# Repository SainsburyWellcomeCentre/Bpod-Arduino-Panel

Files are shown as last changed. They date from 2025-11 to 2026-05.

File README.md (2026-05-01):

# Bpod Arduino Panel



A 58 I/O ports Bpod Module for neuroscience experiments.

> **Note:** To use this module with timing synchronisation, a Bpod state machine is required. Please refer to the [Bpod documentation](https://sanworks.github.io/Bpod_Wiki/) for more information.

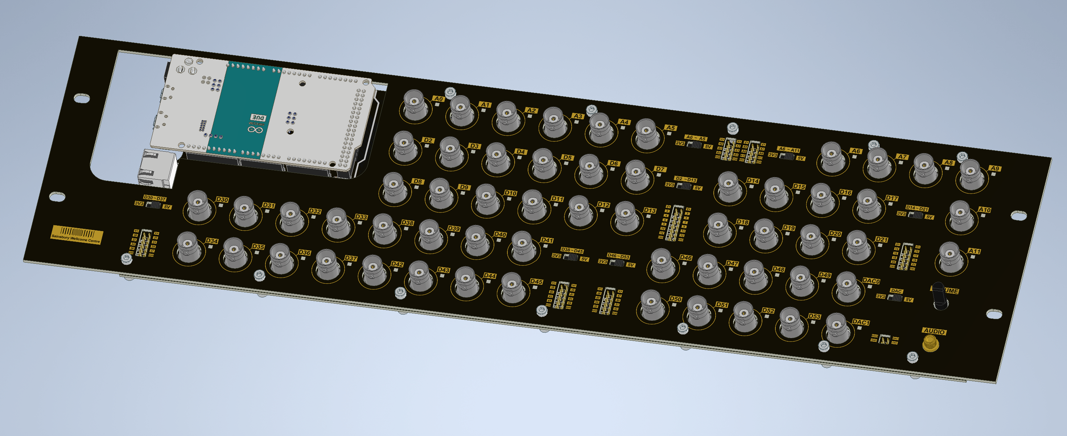
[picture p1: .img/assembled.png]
Assembled


The Bpod Arduino Panel is a Bpod expansion module powered by an Arduino Due. Equipped with 44 digital input/output ports, 12 analogue input ports, and 2 analogue output ports, it can drive various behavioural devices such as lights, speakers, valve drivers, and sensors. Each group of ports can be configured between 5V and 3.3V logic levels. This module is specifically designed for compatibility with the Bpod ecosystem, enabling users to synchronise timing when controlling large numbers of devices.

## 🔧 Features

- 44 digital input/output ports + 14 analogue ports (12 in, 2 out)
- Configurable logic levels (5V/3.3V)
- One 3.5mm audio output drives up to consumer line level (-10 dBV / 0.316 Vrms).
- 3U rack mountable panel

## 🌐 View Online (eCAD)

View the complete electronic design project online via [Altium 365 Viewer](https://sainsburywellcomecentre.github.io/fablabs-documentation/#Bpod-Arduino-Panel)

## 🚀 Getting Started

1. Connect the Bpod Arduino Panel to your computer via USB.
2. Open the Arduino IDE and select the appropriate board and port.
3. Upload the firmware to the Bpod Arduino Panel.
4. Connect the Bpod Arduino Panel to the Bpod state machine using an RJ45 cable.

## 🚀 I/O Port Layout

The following image provides an overview of the port layout and their respective functions.

1. Arduino Due Board
2. RJ45 Connector for Bpod communication
3. Digital I/O Ports (5 groups of 8/12, 44 total)
4. Analogue Input Ports (2 groups of 6, 12 total)
5. Analogue Output Ports (2 total) and Audio Output (3.5mm jack)

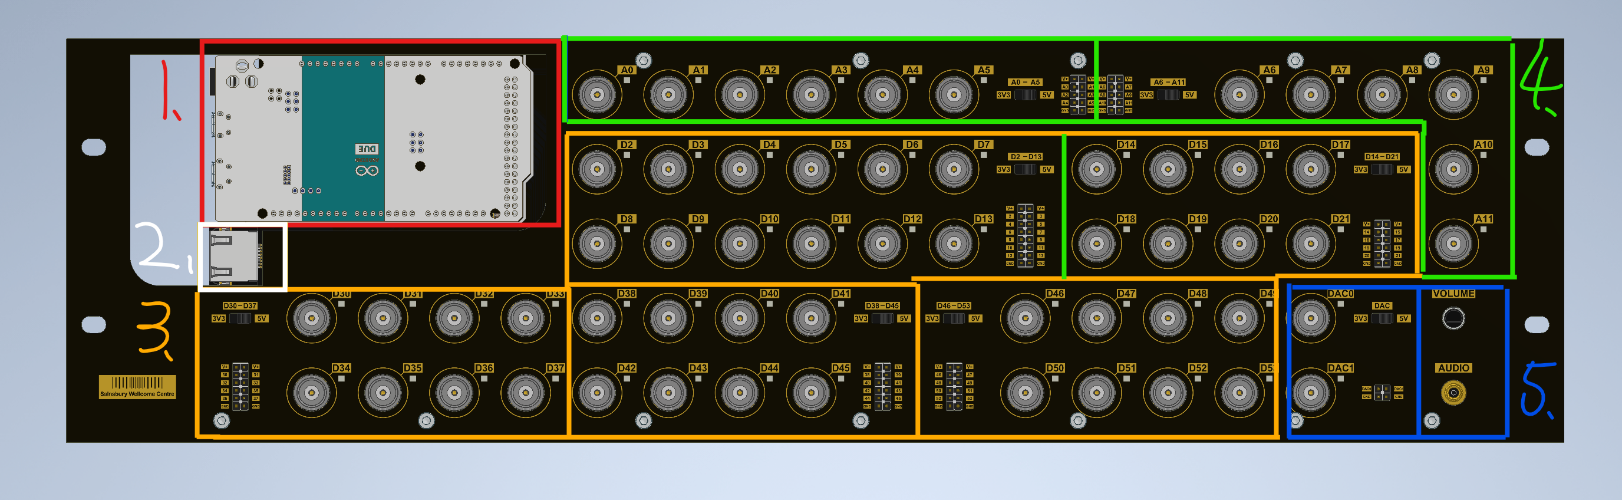
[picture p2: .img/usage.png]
port description


## ⚙️ Voltage Configuration

The max voltage levels for all the I/O are configured by the on-board switches. Each group can be configured between 3.3v and 5V. The ports on the module are grouped as follows:

- D2 to D13
- D14 to D21
- D30 to D37
- D38 to D45
- D46 to D53
- A0 to A5
- A6 to A11
- DAC0 and DAC1

## ⚙️ Firmware and Protocol

The firmware development is based on the Arduino platform, reference from the [Bpod shield](https://github.com/sanworks/Bpod_Gen2/tree/master/Examples/Firmware/Bpod%20Shield) firmware.

The operation code (opcode in Bpod Language) of the device is varied according to the firmware. The functionality of each port has to be pre-defined in the firmware. Please refer to the [opcode table](firmware/OPCODE_TABLE.md) for detailed information on available opcodes and their usage.

## 💻 Software Requirements

- **Altium Designer 24** or newer  
  Academic licenses available via [Altium Education](https://www.altium.com/education/)

- **Autodesk Inventor Pro 2025** or newer  
  Academic licenses via [Autodesk Education](https://www.autodesk.com/education/home)

- **Arduino IDE** (Download from [Arduino Software](https://www.arduino.cc/en/software))

## 📜 License

**Sainsbury Wellcome Centre hardware is released under** [Creative Commons Attribution-ShareAlike 4.0 International](http://creativecommons.org/licenses/by-sa/4.0/).

You are free to:

- **Share** — copy and redistribute the material in any medium or format
- **Adapt** — remix, transform, and build upon the material for any purpose

Under the following terms:

- **Attribution** — Give appropriate credit, link to the license, and indicate changes.
- **ShareAlike** — Distribute your contributions under the same license.
- **No additional restrictions** — Don’t apply legal or technological measures that prevent others from doing anything the license permits.

> For the full legal text, see [LICENSE](LICENSE).

## 💻 TODO

- [ ] Add Python program for standalone operation
- [ ] Add firmware upload instructions
- [ ] Add audio playback firmware example

## 📚 Credits

- **Bpod Shield**: [Sanworks LLC](https://sanworks.github.io/Bpod_Wiki/)
- **Protocol**: [ArCOM](https://github.com/sanworks/ArCOM)

## 🤝 Contributing

1. Fork the repository
2. Create a feature branch
3. Make your changes
4. Submit a pull request

## ❤ Contributors

 <a href = "https://github.com/sainsburywellcomecentre/Bpod-Arduino-Panel/graphs/contributors">
   Contributors
 </a>

## 📧 Contact

- **Author**: [@DCisHurt](https://github.com/DCisHurt)
- **Email**: [yuhsuan.chen@ucl.ac.uk](mailto:yuhsuan.chen@ucl.ac.uk)
- **Website**: [FabLabs](https://sainsburywellcomecentre.github.io/fablabs-documentation/#Bpod-Arduino-Panel)

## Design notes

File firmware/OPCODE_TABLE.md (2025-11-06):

# Opration Code Table

## ADIO.ino

The max voltage levels for all the I/O are configured by the on-board switches. Please refer to the hardware manual for more details.

## Digital Input Events

| Opcode     | Description                      |
| ---------- | -------------------------------- |
| 0x71, 0x72 | D2 Input Event High/Low          |
| 0x73, 0x74 | D3 Input Event High/Low          |
| 0x75, 0x76 | D4 Input Event High/Low          |
| ...        | (other opcodes remain unchanged) |
| 0x97, 0x98 | D21 Input Event High/Low         |

## Digital Input Enable/Disable

| Opcode | Description                      | Byte 1  | Byte 0   |
| ------ | -------------------------------- | ------- | -------- |
| 0x45   | Enable/Disable the digital input | channel | isEnable |

## Digital Output

| Opcode | Description                      | Byte 0 |
| ------ | -------------------------------- | ------ |
| 0x1E   | Set D30 Output High or Low       | logic  |
| 0x1F   | Set D31 Output High or Low       | logic  |
| 0x20   | Set D32 Output High or Low       | logic  |
| ...    | (other opcodes remain unchanged) | ...    |
| 0x35   | Set D53 Output High or Low       | logic  |

## Analog Input reading (16-bits resolution )

| Opcode | Description                      | Byte [1:0] |
| ------ | -------------------------------- | ---------- |
| 0x36   | read A0 voltage                  | ADC [1:0]  |
| 0x37   | read A1 voltage                  | ADC [1:0]  |
| ...    | (other opcodes remain unchanged) | ...        |
| 0x41   | read A11 voltage                 | ADC [1:0]  |

## Analog Output setting (16-bits resolution)

| Opcode | Description      | Byte [1:0] |
| ------ | ---------------- | ---------- |
| 0x42   | Set DAC0 voltage | DAC [1:0]  |
| 0x43   | Set DAC1 voltage | DAC [1:0]  |

## ModuleInfo

| Opcode | Description     |
| ------ | --------------- |
| 0xFF   | Get Module Info |

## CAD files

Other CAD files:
mCAD/HEX Spacer M3x7.ipt
mCAD/PCBA/ARDUINO DUE/ARDUINO DUE.iam
mCAD/PCBA/ARDUINO DUE/Berg Header - 1.27 x 10.ipt
mCAD/PCBA/ARDUINO DUE/Berg Header - 2.54 x 2.ipt
mCAD/PCBA/ARDUINO DUE/Berg Header Receptacle 2.54 x 10 - FCI - 66951-010LF.ipt
mCAD/PCBA/ARDUINO DUE/Berg Header Receptacle 2.54 x 36 - FCI - 66953-018LF.ipt
mCAD/PCBA/ARDUINO DUE/Berg Header Receptacle 2.54 x 8 - FCI - 66951-008LF.ipt
mCAD/PCBA/ARDUINO DUE/Capacitor - Nichicon - UUR1C101MCL1GS.ipt
mCAD/PCBA/ARDUINO DUE/Capacitor.ipt
mCAD/PCBA/ARDUINO DUE/LED - Kingbright - KPT-3216EC.ipt
mCAD/PCBA/ARDUINO DUE/MicroUSB AB - Hirose - ZX62D-AB-5P8.ipt
mCAD/PCBA/ARDUINO DUE/MicroUSB B - Hirose - ZX62D-B-5P8.ipt
mCAD/PCBA/ARDUINO DUE/Microchip - Atmel - SAM3X8EAU.ipt
mCAD/PCBA/ARDUINO DUE/Power Jack - Kycon - KLDHCX-0202-A.ipt
mCAD/PCBA/ARDUINO DUE/Switch - ESwitch - TLE3303.ipt
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

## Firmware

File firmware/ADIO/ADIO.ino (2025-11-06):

#include <Arduino.h>
#include <vector>


// Module setup

char moduleName[] = "BPod Panel"; // Name of module for manual override UI and state machine assembler

#define FirmwareVersion 1
#define InputOffset 2
#define OutputOffset 30

#define nInputChannels 20
#define nOutputChannels 24

#define AinOffset 54
#define AoutOffset 66

#define AinChannels 12
#define AoutChannels 2

uint32_t refractoryPeriod = 300; // Minimum amount of time (in microseconds) after a logic transition on a line, before its level is checked again.
                                  // This puts a hard limit on how fast each channel on the board can spam the state machine with events.

// Constants
#define InputChRangeHigh InputOffset+nInputChannels
#define OutputChRangeHigh OutputOffset+nOutputChannels


std::vector<String> eventNames;

int nEventNames = 0; // Number of behavior events this module can generate, 2 for each input channel (high and low)

// Variables
byte opCode = 0;
byte channel = 0;
byte state = 0;
byte thisEvent = 0;
boolean readThisChannel = false; // For implementing refractory period (see variable above)
byte inputChState[nInputChannels] = {0}; // Current state of each input channel
byte lastInputChState[nInputChannels] = {0}; // Last known state of each input channel
byte inputsEnabled[nInputChannels] = {0}; // For each input channel, enabled or disabled
uint32_t inputChSwitchTime[nInputChannels] = {0}; // Time of last detected logic transition
byte events[nInputChannels*2] = {0}; // List of high or low events captured this cycle
byte nEvents = 0; // Number of events captured in the current cycle
uint32_t currentTime = 0; // Current time in microseconds

void setup()
{
  // Serial.begin(115200);
  Serial.begin(1312500);
  SerialUSB.begin(1312500);
  currentTime = micros();
  for (int i = 0; i < nInputChannels; i++) {
    pinMode(i+InputOffset, INPUT_PULLUP);
    inputsEnabled[i] = 1;
    inputChState[i] = 1;
    lastInputChState[i] = 1;
    eventNames.push_back(String(i+InputOffset) + "_Hi");
    eventNames.push_back(String(i+InputOffset) + "_Lo");
    nEventNames += 2;
  }
  for (int i = OutputOffset; i < OutputChRangeHigh; i++) {
    pinMode(i, OUTPUT);
  }
  analogReadResolution(16); // Set analog read resolution to 16 bits
  analogWriteResolution(16); // Set analog write resolution to 16 bits
  analogWrite(DAC0, 0);
  analogWrite(DAC1, 0);
}

void loop()
{
  currentTime = micros();

if (Serial.available()) {
    opCode = Serial.read();
    if (opCode == 255) {
      returnModuleInfo();
    } 
    else if ((opCode >= OutputOffset) && (opCode < OutputChRangeHigh)) {
      state = Serial.read();
      digitalWrite(opCode,state); 
    }
    else if ((opCode >= AinOffset) && (opCode < AinOffset + AinChannels)) {
      returnAnalogRead(opCode);
    } 
    else if ((opCode >= AoutOffset) && (opCode < AoutOffset + AoutChannels)) {
      state = Serial.read();
      int val = (Serial.read() << 8) + Serial.read();
      analogWrite(opCode,val);
    }
    else if (opCode == 'E') {
      channel = Serial.read();
      state = Serial.read();
      if ((channel >= InputOffset) && (channel < InputChRangeHigh)) {
        inputsEnabled[channel-InputOffset] = state;
      }
    }
  }

  if (SerialUSB.available()) {
    opCode = SerialUSB.read();
    if (opCode == 255) {
      returnModuleInfo_USB();
    } 
    else if ((opCode >= OutputOffset) && (opCode < OutputChRangeHigh)) {
      state = SerialUSB.read();
      digitalWrite(opCode,state); 
    }
    else if ((opCode >= AinOffset) && (opCode < AinOffset + AinChannels)) {
      returnAnalogRead_USB(opCode);
    } 
    else if ((opCode >= AoutOffset) && (opCode < AoutOffset + AoutChannels)) {
      int val = (SerialUSB.read() << 8);
      val += SerialUSB.read();
      analogWrite(opCode,val);
    }
    else if (opCode == 'E') {
      channel = SerialUSB.read();
      state = SerialUSB.read();
      if ((channel >= InputOffset) && (channel < InputChRangeHigh)) {
        inputsEnabled[channel-InputOffset] = state;
      }
    }
  }

  thisEvent = 1;
  for (int i = 0; i < nInputChannels; i++) {
    if (inputsEnabled[i] == 1) {
      inputChState[i] = digitalRead(i+InputOffset);
      readThisChannel = false;
      if (currentTime > inputChSwitchTime[i]) {
        if ((currentTime - inputChSwitchTime[i]) > refractoryPeriod) {
          readThisChannel = true;
        }
      } else if ((currentTime + 4294967296-inputChSwitchTime[i]) > refractoryPeriod) {
        readThisChannel = true;
      }
      if (readThisChannel) {
        if ((inputChState[i] == 1) && (lastInputChState[i] == 0)) {
          events[nEvents] = thisEvent+0x70; nEvents++;
          inputChSwitchTime[i] = currentTime;
          lastInputChState[i] = inputChState[i];
        }
        if ((inputChState[i] == 0) && (lastInputChState[i] == 1)) {
          events[nEvents] = thisEvent+1+0x70; nEvents++;
          inputChSwitchTime[i] = currentTime;
          lastInputChState[i] = inputChState[i];
        }
      }
    }
    thisEvent += 2;
  }
  if (nEvents > 0) {
    Serial.write(events, nEvents);
    SerialUSB.write(events, nEvents);
    nEvents = 0;
  }
}

void returnAnalogRead_USB(int channel){

  SerialUSB.write((byte)channel);
  int value = analogRead(channel);
  SerialUSB.write((byte)(value >> 8));
  SerialUSB.write((byte)(value & 0xFF));
}

void returnModuleInfo_USB() {

  SerialUSB.write(65); // Acknowledge

  SerialUSB.write((byte)((FirmwareVersion >> 24) & 0xFF)); // 4-byte firmware version
  SerialUSB.write((byte)((FirmwareVersion >> 16) & 0xFF));
  SerialUSB.write((byte)((FirmwareVersion >> 8) & 0xFF));
  SerialUSB.write((byte)(FirmwareVersion) & 0xFF);

  SerialUSB.write((byte)(sizeof(moduleName)-1));
  SerialUSB.write((byte*)moduleName, sizeof(moduleName)-1); // Module name

  SerialUSB.write((byte)0x01); // 1 if more info follows, 0 if not

  SerialUSB.write('#'); // Op code for: Number of behavior events this module can generate
  SerialUSB.write(nInputChannels*2); // 2 states for each input channel

  SerialUSB.write((byte)0x01); // 1 if more info follows, 0 if not

  SerialUSB.write('E'); // Op code for: Behavior event names
  SerialUSB.write((byte)nEventNames);

  for (int i = 0; i < nEventNames; i++) { // Once for each event name
    SerialUSB.write(eventNames[i].length()); // Send event name length
    SerialUSB.write((byte*)eventNames[i].c_str(), eventNames[i].length()); // Send event name
  }

  SerialUSB.write((byte)0x00); // 1 if more info follows, 0 if not

}

void returnAnalogRead(int channel){

  Serial.write((byte)channel);
  int value = analogRead(channel);
  Serial.write((byte)(value >> 8));
  Serial.write((byte)(value & 0xFF));
}

void returnModuleInfo() {

  Serial.write(65); // Acknowledge

  Serial.write((byte)((FirmwareVersion >> 24) & 0xFF)); // 4-byte firmware version
  Serial.write((byte)((FirmwareVersion >> 16) & 0xFF));
  Serial.write((byte)((FirmwareVersion >> 8) & 0xFF));
  Serial.write((byte)(FirmwareVersion) & 0xFF);

  Serial.write((byte)(sizeof(moduleName)-1));
  Serial.write((byte*)moduleName, sizeof(moduleName)-1); // Module name

  Serial.write((byte)0x01); // 1 if more info follows, 0 if not

  Serial.write('#'); // Op code for: Number of behavior events this module can generate
  Serial.write(nInputChannels*2); // 2 states for each input channel

  Serial.write((byte)0x01); // 1 if more info follows, 0 if not

  Serial.write('E'); // Op code for: Behavior event names
  Serial.write((byte)nEventNames);

  for (int i = 0; i < nEventNames; i++) { // Once for each event name
    Serial.write(eventNames[i].length()); // Send event name length
    Serial.write((byte*)eventNames[i].c_str(), eventNames[i].length()); // Send event name
  }

  Serial.write((byte)0x00); // 1 if more info follows, 0 if not

}

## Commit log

2025-10-28 add CAD files
    [6339160-1_CMP-390-0000-8.ipt, ARDUINO DUE.iam, Analog Input Connector.SchDoc, Analog Input.SchDoc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]
2025-11-05 add soruce files
    [Analog Input Connector.SchDoc, Analog Input.SchDoc, Arduino Due.SchDoc, BPod Panel Due - 3U Panel.PcbDoc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]
